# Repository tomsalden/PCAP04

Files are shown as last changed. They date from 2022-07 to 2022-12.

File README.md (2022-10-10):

# ESP32 firmware for the PCAP04

This project has been written as part of a Master's Thesis at the [University of Technology in Delft](https://www.tudelft.nl/). The thesis is based around a Silicon Carbide MEMS pressure sensor. This sensor is a capacitor-based sensor and to read it out, a Capacitor-to-digital converter is necessary. The PCAP04 should work really well due to its high accuracy and resolution. In addition, because it can measure up to 6 capacitances and compare it to one reference capacitance, it is ideal for multiple sensors in the same envionment.
A PlatformIO project has been added to this repository for easy deployment of the code. This contains the latest code written.

# Connecting to the PCAP04

This firmware is written for the ESP32 DevKit-WROOM (available in the Makerspace from the Electrical Engineering Study Association: [Klushok](https://klushok.etv.tudelft.nl/)).

The heart of the firmware uses a library written by Törehan. It has been rewritten to let it make use of I2C in stead of SPI. The reason is that SPI would not work consistenly for my set-up.
The original library can be found on his [GitHub page](https://github.com/torehan/pcap04-arduino).

An example of his integration of the library is visible on his [Metsensor page](https://github.com/torehan/metsensor-pio)

The firmware was first developed for the [PCAP04-EVA-Kit](https://nl.mouser.com/ProductDetail/ScioSense/PCAP04-EVA-KIT?qs=YCa%2FAAYMW01pCMwt%2Fq6O1Q%3D%3D). Later on, the firmware is updated for usage of a custom PCB. In theory, the EVA-Kit should still work with some small modifications. The pinout and further instructions can be found from the section [PCAP04-EVA-board instructions](OldReadme.md). The next sections describe the project using the custom PCB.

# Custom measurement PCB

The PCB has space for three PCAP04 CDC's. Each CDC can read 4 to 5 capacitances and has 1 reference capacitor to make sure the base value is correct.
1 Li-Ion battery will be attached at the back to power the board. Afterwards, the battery is protected and the voltage is boosted to 5V with a HW-775.
As an alternative, one PCAP04 EVA Board can be used instead of one PCAP04 bare chip.

The frontside of the PCB:

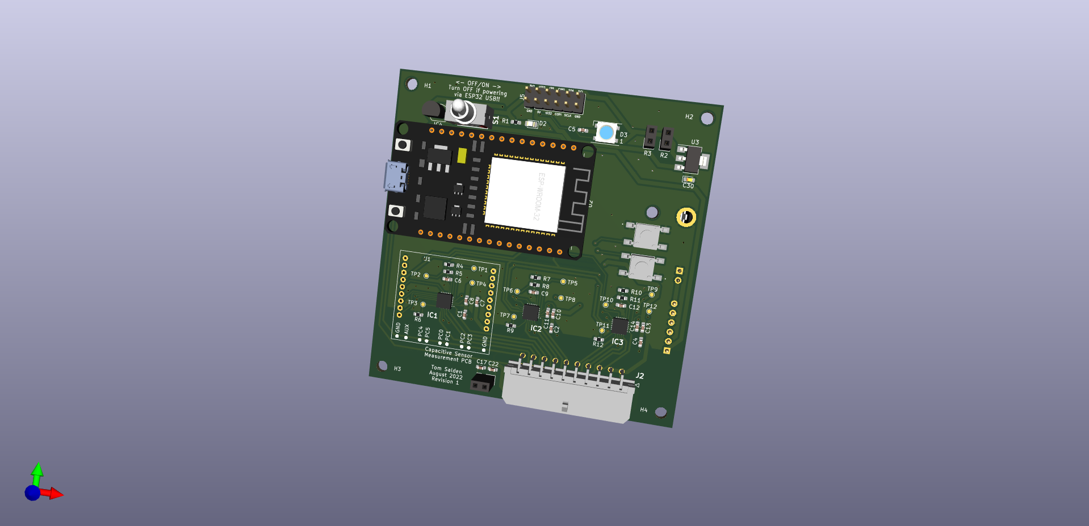
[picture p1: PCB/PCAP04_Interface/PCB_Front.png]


The backside of the PCB:

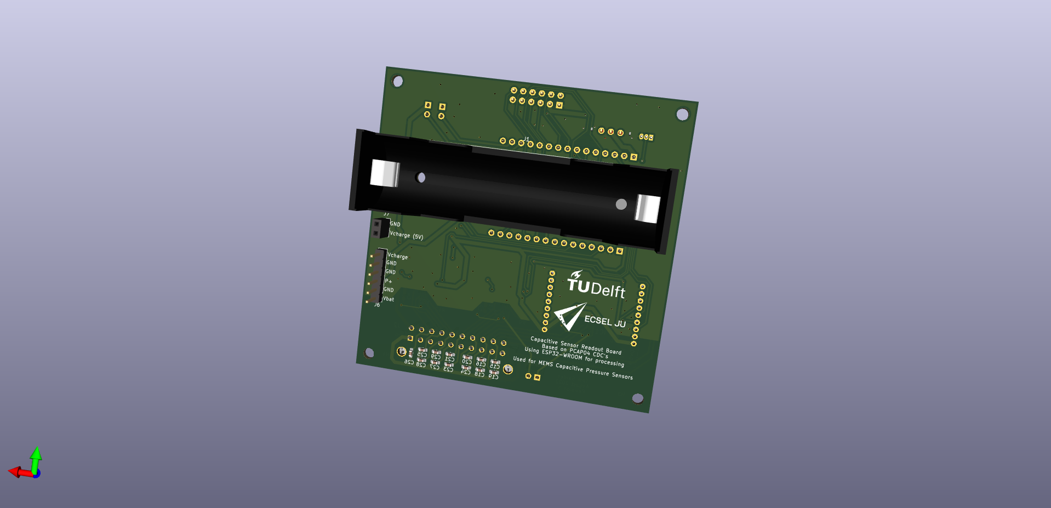
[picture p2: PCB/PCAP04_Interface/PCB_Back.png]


The PCB design includes the following features:

- 3 PCAP04 (or older) measurement chips.
- 1 PCAP04 chip can be replaced with a PCAP04-EVA-BOARD (for testing purposes)
- 3 on-PCB reference capacitors
- 15 (grounded) capacitor measurement possibilities
- Optional offset capacitors can be placed

<!-- -->

- 2 lines for piezoresistive readout are added using voltage dividers
- External resistors can be placed for the voltage division

<!-- -->

- ESP32-Wroom to connect to the PCAP04 chips and process the data
- Micro-SD card holder to save the data
- Power LED directly connected to power line
- RGB Led that is controlled by the ESP32
- 2 multipurpose buttons (start/stop measurements etc.)
- Temperature sensor to keep track of ambient temperature

<!-- -->

- On-off switch breaking the power line
- Can be powered by 2x Li-Ion 18650 batteries (No protection circuitry, use at own risk! Reverse polarity protection is included)
- Cam also be powered by 5V USB line in ESP32-wroom

The Bill of Materials can be found [here]([PCB/PCAP04_Interface/bom/ibom.html](https://tomsalden.github.io/PCAP04/PCB/PCAP04_Interface/bom/ibom.html)) and the order list is placed [here](PCB/PCAP04_Interface/bom/Farnell_Order_List.xlsx).

# Programming instructions
The project has been included in a PlatformIO folder. To setup the workspace, PlatformIO has to be downloaded and this folder has to be imported as a project. This should automatically set the correct libraries and settings. The firmware can be uploaded to an ESP-32 once the project has been imported.

# Program Instructions
Once the firmware has been compiled and uploaded and the PCB has been manufactured, the measurement PCB is ready to start measuring. Place an empty SD card in the SD card slot. Put in a battery in the holder and turn on the switch. The PCB will start its measurements.

## First run
 When the system is turned on, first the program will generate configuration files. Four configuration files in total, one for each PCAP04 chip and one general configuration file.
 
 The general configuration file will define the wifi network the system will try to connect to. The PCAP configuration files define the configuration that can be changed in the webserver.
 
 After this, the system will start with the default settings. It will search for a Wifi Network called "GenericWifi-SSID" with the password "GenericWifi-PWD". If this is not found, then it will create a hotspot.
 Afterwards, the system will apply the default configuration for the PCAP chips and startup a webserver. This can be accessed at the address "192.168.4.1".

 ## Further operation
 Once the system has been stared once, the general configurations file can be edited to let the ESP32 connect to a specified wifi network at startup. If this is not found, the system will create a hotspot.

 Any changes in the webserver settings will immediately be written to the SD card in the corresponding configuration file. This means that at startup, the chips will be loaded with the newest configuration.

 ## Data
 The ESP32 collects the data from all chips. In addition, the system will print a time and a temperature at the time of the measurement. The data file that is generated is a text-based file that can be interpreted as a csv file.

 ### Time
 The measurement of the chips are timed, and the output that will be written will correspond to the time they are taken.
 Because the system does not have a Real Time Clock (RTC), the ESP32 does not know the time at startup. Therefore, the default time is set at October 18 2022 at 0:00. To set the time and date to the correct moment, connect to the webserver and press the "Set Current Time" button. From that moment on, the time will be synchronised with the device that pressed on that button until the ESP32 is restarted.

 ### Temperature
 The temperature on the PCB is measured using a MCP-9701. The voltage reading is converted to a temperature and saved in the data files.

 ### Capacitance data
 The capacitance of each pin of every PCAP chip is read out as fast as possible. When this is done, the data is collected and written to the data file.

## Indication LED
The PCB features an indication LED. This LED shows the status of the program.
After startup and configuration, the measurement starts and the LED will blink blue-green.

# Features and Future improvements

✅Ability to connect to and read data from PCAP04

✅Ability to change I2C address on demand

✅Read data synchronously with PCAP04, as recommended in the datasheet

✅Add SD-card to the system to log data

✅Place PCAP04 settings file on SD card

✅Create a PCB for this system

✅Edit PCAP04 settings without reflashing ESP32

✅Create webserver-based interface for ESP32 (for config changes)

✅Allow for three PCAP04 devices at the same time

✅Clean up code for deployment

⬜️~~Automatically change output format depending on mode selection~~

⬜️~~Make a csv file automatically from the output~~

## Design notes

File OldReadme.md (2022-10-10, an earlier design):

# PCAP04-EVA-board instructions

## Interconnections PCAP04-Dev-Kit and ESP32 DevKit-WROOM

The interconnects used for the current firmware. The following images show the pinout of the [ESP32 board](https://raw.githubusercontent.com/AchimPieters/esp32-homekit-camera/master/Images/ESP32-30PIN-DEVBOARD.png) and the PCAP04.

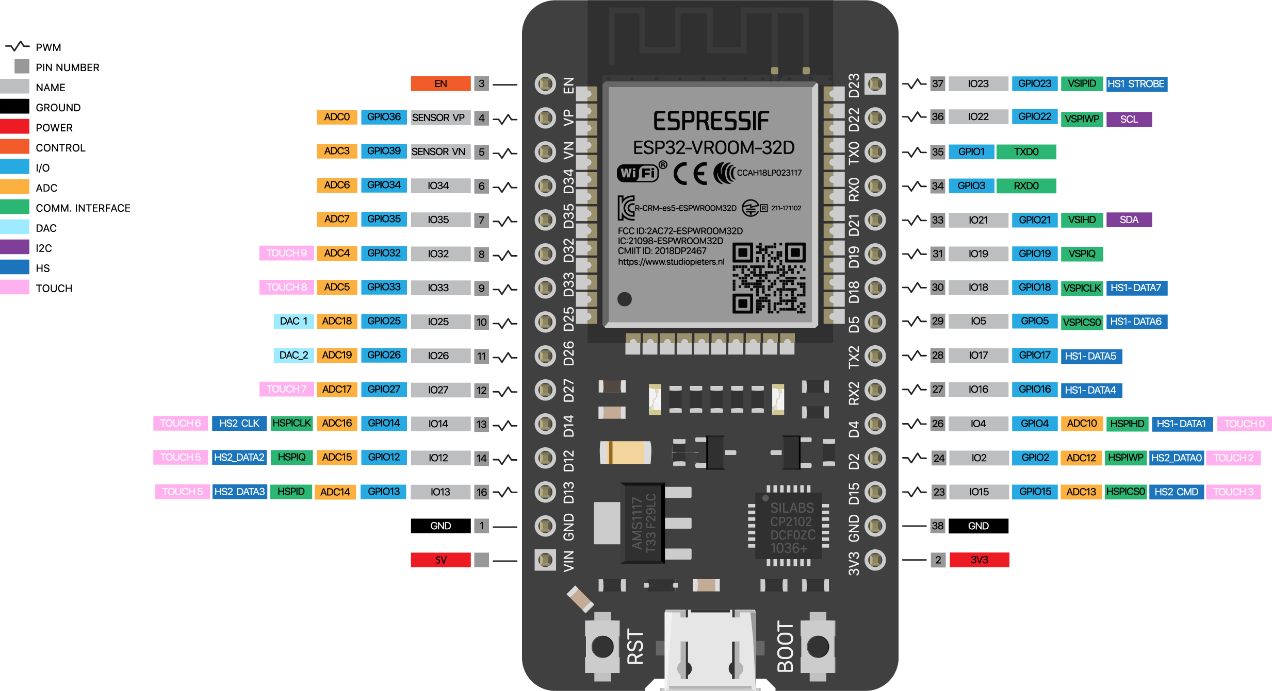
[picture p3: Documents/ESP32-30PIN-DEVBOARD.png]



### Power

| ESP32 | PCAP04                               |
| ----- | ------------------------------------ |
| 3V3   | VDD (J1.1 or J2.1)                   |
| GND   | GND (J1.2, J1.9, J2.2, J2.7 or J2.9) |

### Communication

| ESP32          | PCAP04          |
| -------------- | --------------- |
| 3V3            | IIC_EN (J2.3)   |
| GPIO21-I2C SDA | MOSI_SDA (J2.4) |
| GPIO22-I2C SCL | SCK_SCL (J2.6)  |

| ESP32            | SD-Card Reader |
| ---------------- | -------------- |
| 3V3              | +3.3           |
| GND              | GND            |
| GPIO5-VSPI CS0   | CS             |
| GPIO18-VSPI CLK  | SCK            |
| GPIO19-VSPI MISO | MISO           |
| GPIO23-VSPI MOSI | MOSI           |

### GPIO connections

| ESP32  | PCAP04     |
| ------ | ---------- |
| GPIO2  | PG5 (J1.8) |
| GPIO4  | PG4 (J1.7) |
| GPIO16 | PG3 (J1.6) |
| GPIO17 | PG2 (J1.5) |

### Other connections

| ESP32  | Interface |
| ------ | --------- |
| GPIO32 | Led Blue  |
| GPIO33 | Led Green |
| GPIO26 | Led Red   |
| GPIO27 | Power Led |

## Flashing the firmware

For flashing the firmware, the basic Arduino IDE can be used. The board settings used are:

- Board:            Node32s
- Upload Speed:     921600
- Flash Frequency   80MHz
- Partition Scheme  Default
- Core Debug Level  None

## Using the Set-up

At this point in time, the set-up works via the serial monitor and a limited web-interface. The following will happen at startup:

1. The ESP32 will startup, displayed with the Power Led. Either it will connect to a known network or start its own network.
2. The ESP32 will test if an SD card is available. It will create a new file for data storage. If the SD-card is not available, the indicator light will flash red three times.
3. The ESP32 will check if a config file is present on the SD. If so, the config will be loaded. Otherwise, a new file will be created with the standard configuration.
4. The ESP will test the I2C connection to the PCAP04. If there is a problem, a red light will appear. Otherwise the light turns blue
5. The ESP will initialise the PCAP04 and write the correct configuration to the chip. Once done, the Led turns green
6. After initialisation, the PCAP04 will start its measurements. The ESP32 will retreive a new measurement every second, indicated by a flashing red-green light.
7. If an SD-card is available, the ESP32 will save the data as in a .csv format on the card. In addition, the ESP32 will display the current measurement values in the serial port. (If a more complete output is necessary, uncomment line 204 in the [PCAP04.ino](https://github.com/tomsalden/PCAP04/blob/main/PCAP04.ino#L192) file and comment the Print for Excel lines.)

Now, the Serial Port of the Arduino IDE can be used to readout the values.
In addition, the [Data Streamer](https://support.microsoft.com/nl-nl/office/wat-is-data-streamer-1d52ffce-261c-4d7b-8017-89e8ee2b806f) in Excel can record, process and save live data.

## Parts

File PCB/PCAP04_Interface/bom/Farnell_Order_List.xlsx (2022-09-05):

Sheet: Sheet1
Part Number | Quantity | Description | Price/piece | Price total | Other websites | Part name | Quantity | website | Price/piece | Piece total
2896375 | 30 | SMD Multilayer Ceramic Capacitor, 1 pF | €0.1080 | €3.2400 |  | WS2812B (https://www.vanallesenmeer.nl/WS2812B-5050-RGB-LED-with-Integrated-Driver-Chip-10-Pack-Adafruit-1655) | 1 | vanallesenmeer | €8.35 | €8.35 | Total
2134025 | 6 | SMD Multilayer Ceramic Capacitor, 2 pF | €0.3230 | €1.9380 |  | Verzendkosten | 1 | vanallesenmeer | €2.00 | €2.00 | €145.49
2672793 | 6 | SMD Multilayer Ceramic Capacitor, IR Reflow, 10000 | €0.1180 | €0.7080 |  | AMS1117 3V3 (https://www.tinytronics.nl/shop/en/components/voltage-regulators/ams1117-3.3v-voltage-regulator-sot-223) | 2 | tinytronics | €0.50 | €1.00
2494230 | 10 | SMD Multilayer Ceramic Capacitor, 10 µF | €0.0589 | €0.5890 |  | Li-Ion Charging circuit (https://www.tinytronics.nl/shop/en/power/bms-and-chargers/li-ion-and-li-po/with-protection-circuit/li-ion-charge-and-protection-circuit-2100ma-with-dc-dc-conv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) | 2 | tinytronics | €4.00 | €8.00
3416132 | 10 | SMD Multilayer Ceramic Capacitor, 4.7 µF | €0.1130 | €1.1300 |  | 18650 battery holder (https://www.tinytronics.nl/shop/en/power/battery-holders-and-clips/18650/1x-18650-battery-holder-for-pcb) | 2 | tinytronics | €1.50 | €3.00
2672791 | 2 | SMD Multilayer Ceramic Capacitor, IR Reflow, 0.1 µF | €0.2360 | €0.4720 |  | Verzendkosten | 1 | tinytronics | €2.50 | €2.50
197427 | 5 | Surface Mount Tantalum Capacitor, 10 µF | €0.3000 | €1.5000
2331324 | 2 | SMD Chip Resistor, 64.9 ohm | €0.3990 | €0.7980
3796325 | 5 | LED, Red, SMD | €0.1210 | €0.6050
1466783 | 8 | Standoff, Zinc Plated | €0.4610 | €3.6880
3397776 | 10 | Tactile Switch, FSMJSM | €0.2850 | €2.8500
1439483 | 2 | Temperature Sensor IC, Voltage, ± 2°C, 0 °C, 70 °C, TO-92, 3 Pins | €0.4800 | €0.9600
 |  |  |  | €0.0000
 |  |  |  | €0.0000
Mouser
Part Number | Quantity | Description | Price/piece | Price total
985-PCAP04-AQFM-24 | 10 | PCAP04 | €6.8600 | €68.6000
118-2MS1T2B3M2QES | 2 | Toggle Switch | €3.1700 | €6.3400
538-43045-2022 | 2 | Headers & Wire Housings Microfit 3.0 | €8.2100 | €16.4200
640-MEM20670218000A | 2 | Micro SDCard Holder | €1.1400 | €2.2800
DigiKey
Part Number | Quantity | Description | Price/piece | Price total
BH-18650-PC-ND | 2 | 18650 Battery holder | €4.2600 | €8.5200

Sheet: EverythingMouser
Mouser number | Manufactuer number | Quantity | Description | Price/piece | Price total
77-VJ0603A1R0BXACBC | VJ0603A1R0BXACW1BC | 30 | SMD Multilayer Ceramic Capacitor, 1 pF | €0.114 | €3.42
77-VJ0603D2R0BXPAJ | VJ0603D2R0BXPAJ | 6 | SMD Multilayer Ceramic Capacitor, 2 pF | €0.470 | €2.82
791-0603B103K101CT | 0603B103K101CT | 10 | SMD Multilayer Ceramic Capacitor, IR Reflow, 10000 | €0.029 | €0.29
81-R188R60J106KE7D | GRM188R60J106KE47D | 10 | SMD Multilayer Ceramic Capacitor, 10 µF | €0.059 | €0.59
810-C1608X7S1A475MAC | C1608X7S1A475M080AC | 10 | SMD Multilayer Ceramic Capacitor, 4.7 µF | €0.119 | €1.19
80-C0603C104J4R | C0603C104J4RACTU | 2 | SMD Multilayer Ceramic Capacitor, IR Reflow, 0.1 µF | €0.100 | €0.20
581-F981A226MMALZT | F981A226MMALZT | 2 | Surface mount talantum Cap 22uF | €0.700 | €1.40
667-ERA-3AEB64R9V | ERA-3AEB64R9V | 2 | SMD Chip Resistor, 64.9 ohm | €0.350 | €0.70
710-150080RS75000 | 150080RS75000 | 5 | LED, Red, SMD | €0.190 | €0.95
710-970250321 | 970250321 | 8 | Standoff, Zinc Plated | €0.580 | €4.64
506-FSM2JSMAATR | FSM2JSMAATR | 4 | Tactile Switch, FSMJSM | €0.320 | €1.28
579-MCP9701-E/TO | MCP9701-E/TO | 2 | Temperature Sensor IC, Voltage, ± 2°C, 0 °C, 70 °C, TO-92, 3 Pins | €0.570 | €1.14
48SM003 | 48SM003 | 8 | M3 screw | €0.194 | €1.55
985-PCAP04-AQFM-24 | PCAP04-AQFM-24 | 10 | PCAP04 | €6.16 | €61.60
118-2MS1T2B3M2QES | 2MS1T2B3M2QES | 2 | Toggle Switch | €3.17 | €6.34
538-43045-2022 | 43045-2022 | 2 | Headers & Wire Housings Microfit 3.0 | €8.21 | €16.42
640-MEM20670218000A | MEM2067-02-180-00-A | 2 | Micro SDCard Holder | €1.14 | €2.28
485-4684 | 4684 | 1 | 2020 RGB LEDs - 10-pack - WS2812B | €3.95 | €3.95
637-LDI1117-3.3H | LDI1117-3.3H | 2 | 3.3 LDO | €1.960 | €3.92
538-43025-2000 | 43025-2000 | 5 | Mouser recepticle | €1.330 | €6.65
538-43030-0004-CT | 43030-0004 (Cut Strip) | 100 | Mouser contacts | €0.082 | €8.20
Shopping cart link | https://nl.mouser.com/ProjectManager/ProjectDetail.aspx?AccessID=6550a5fe31 |  |  |  | €129.53

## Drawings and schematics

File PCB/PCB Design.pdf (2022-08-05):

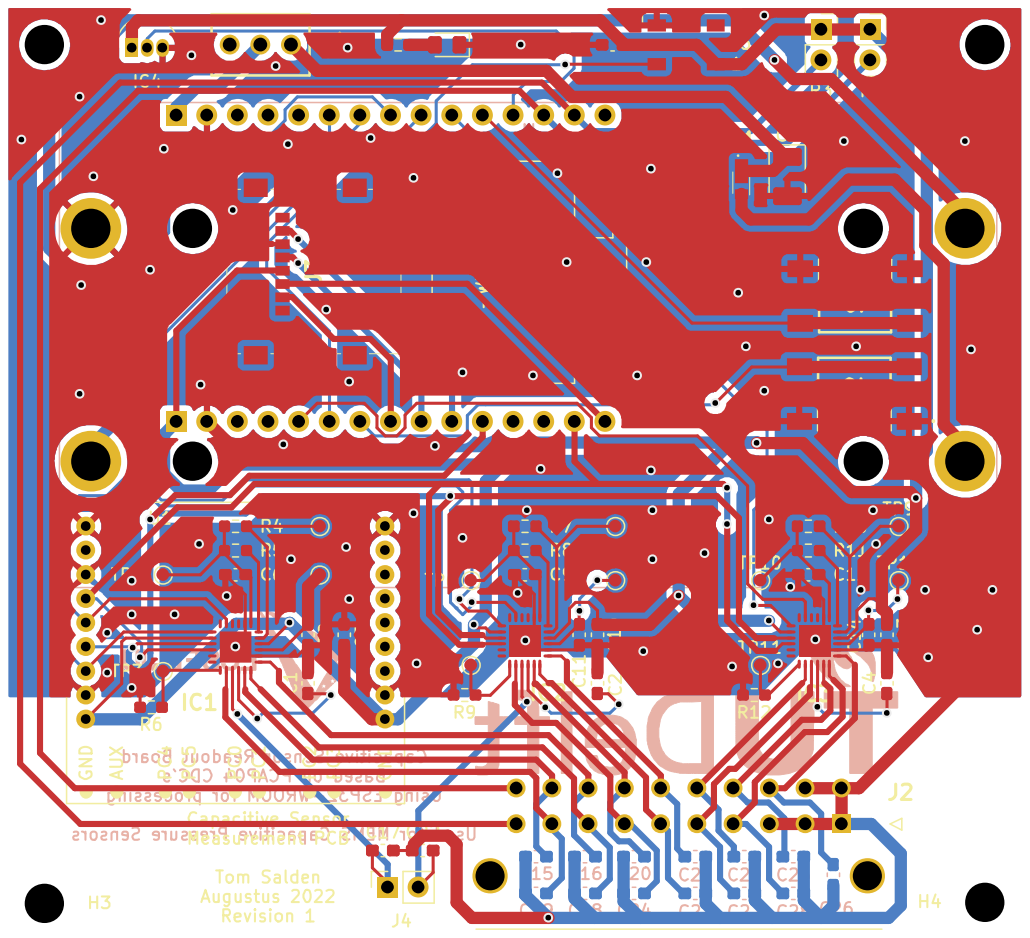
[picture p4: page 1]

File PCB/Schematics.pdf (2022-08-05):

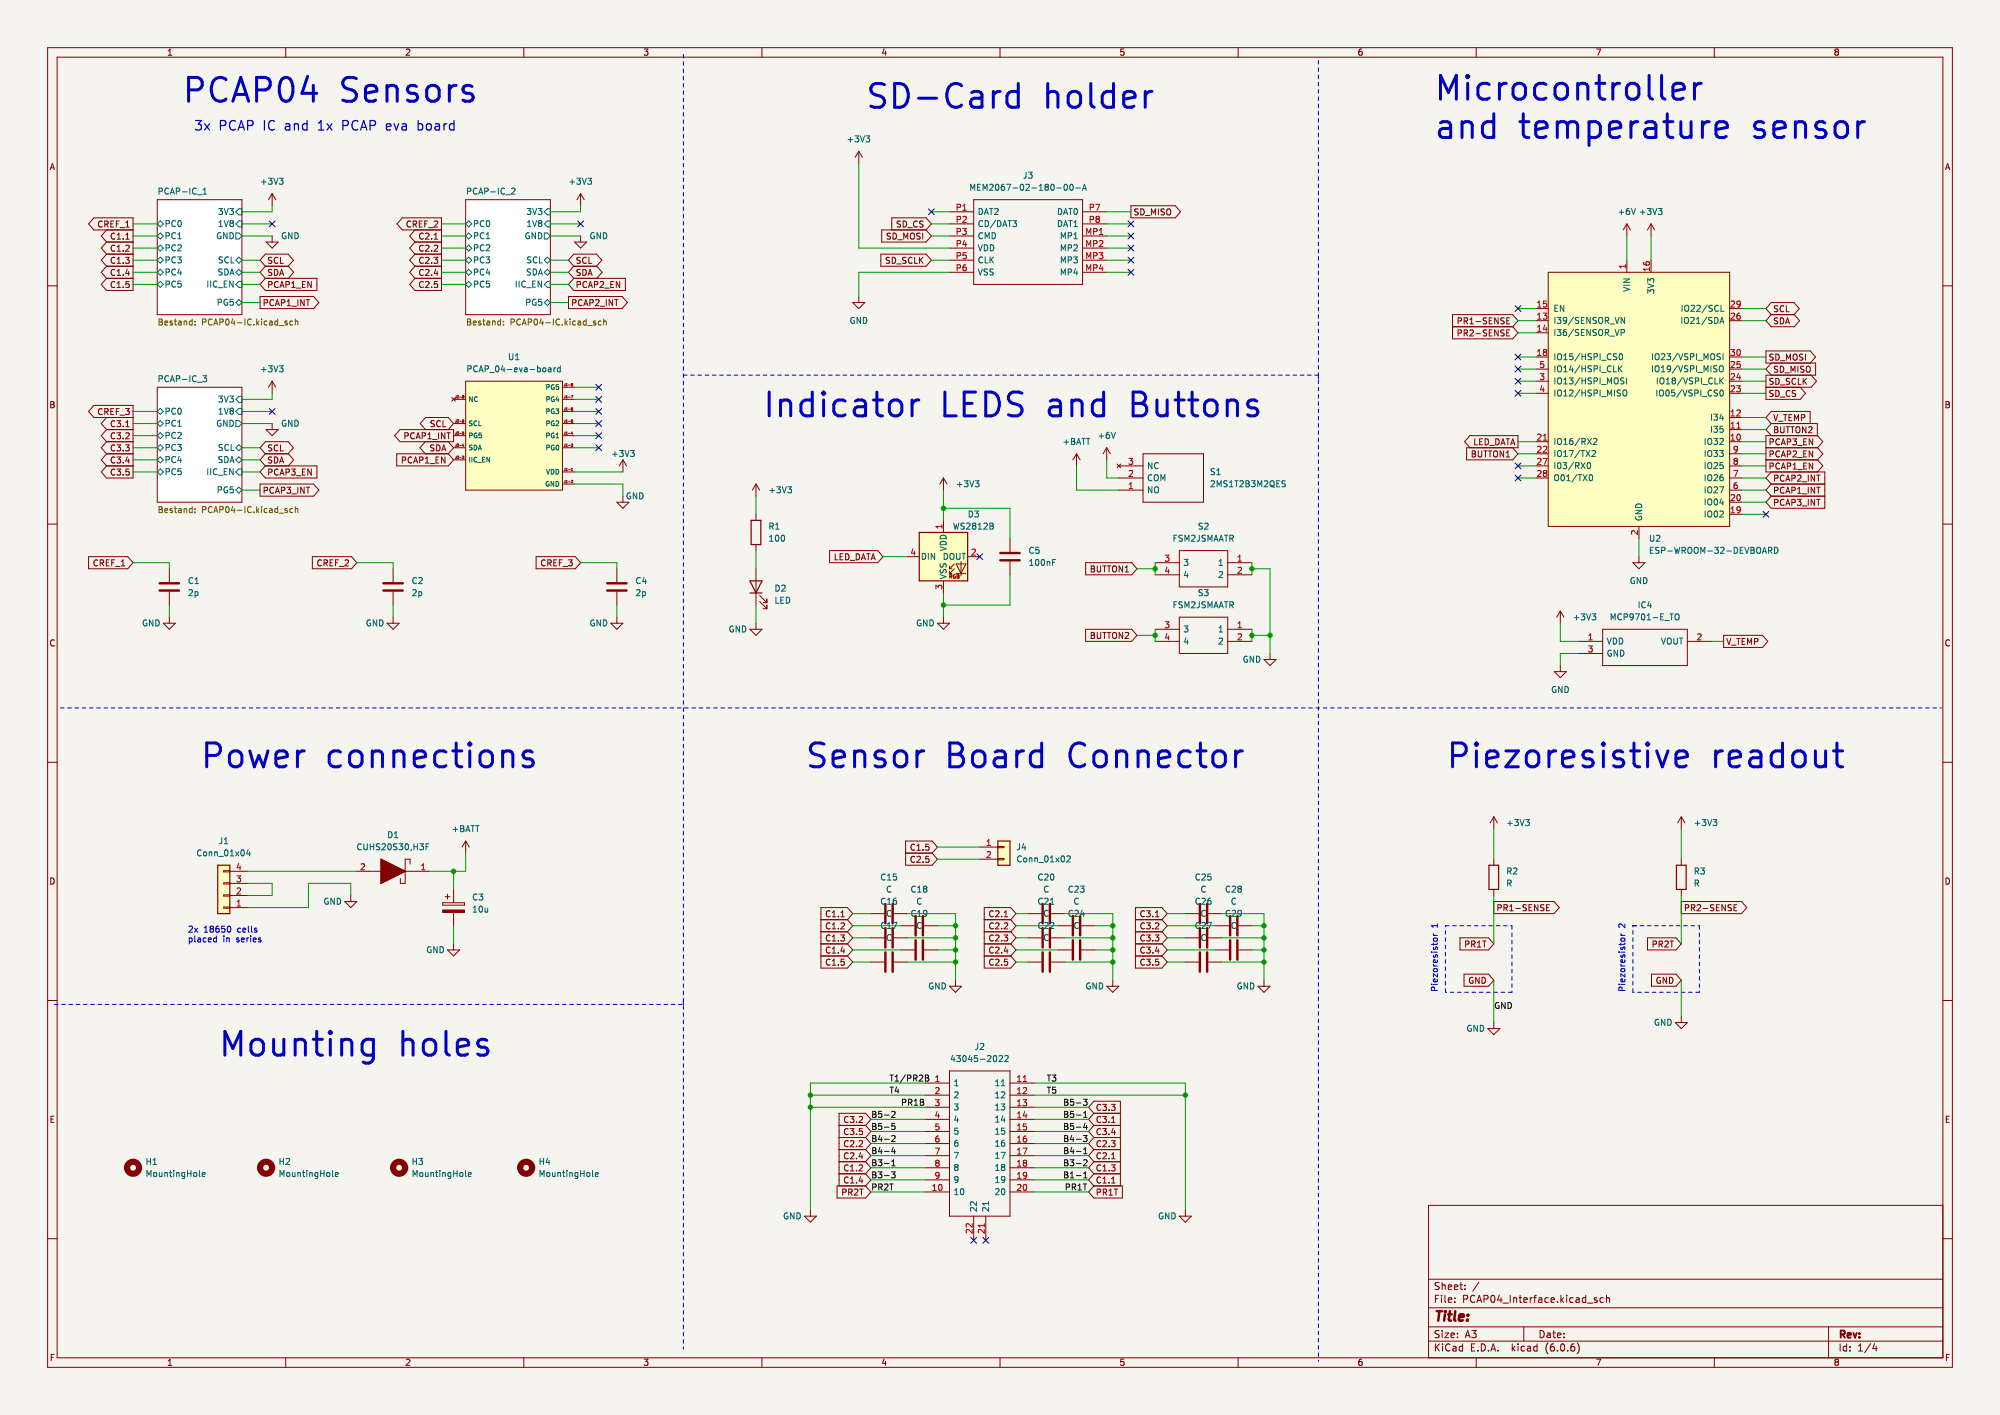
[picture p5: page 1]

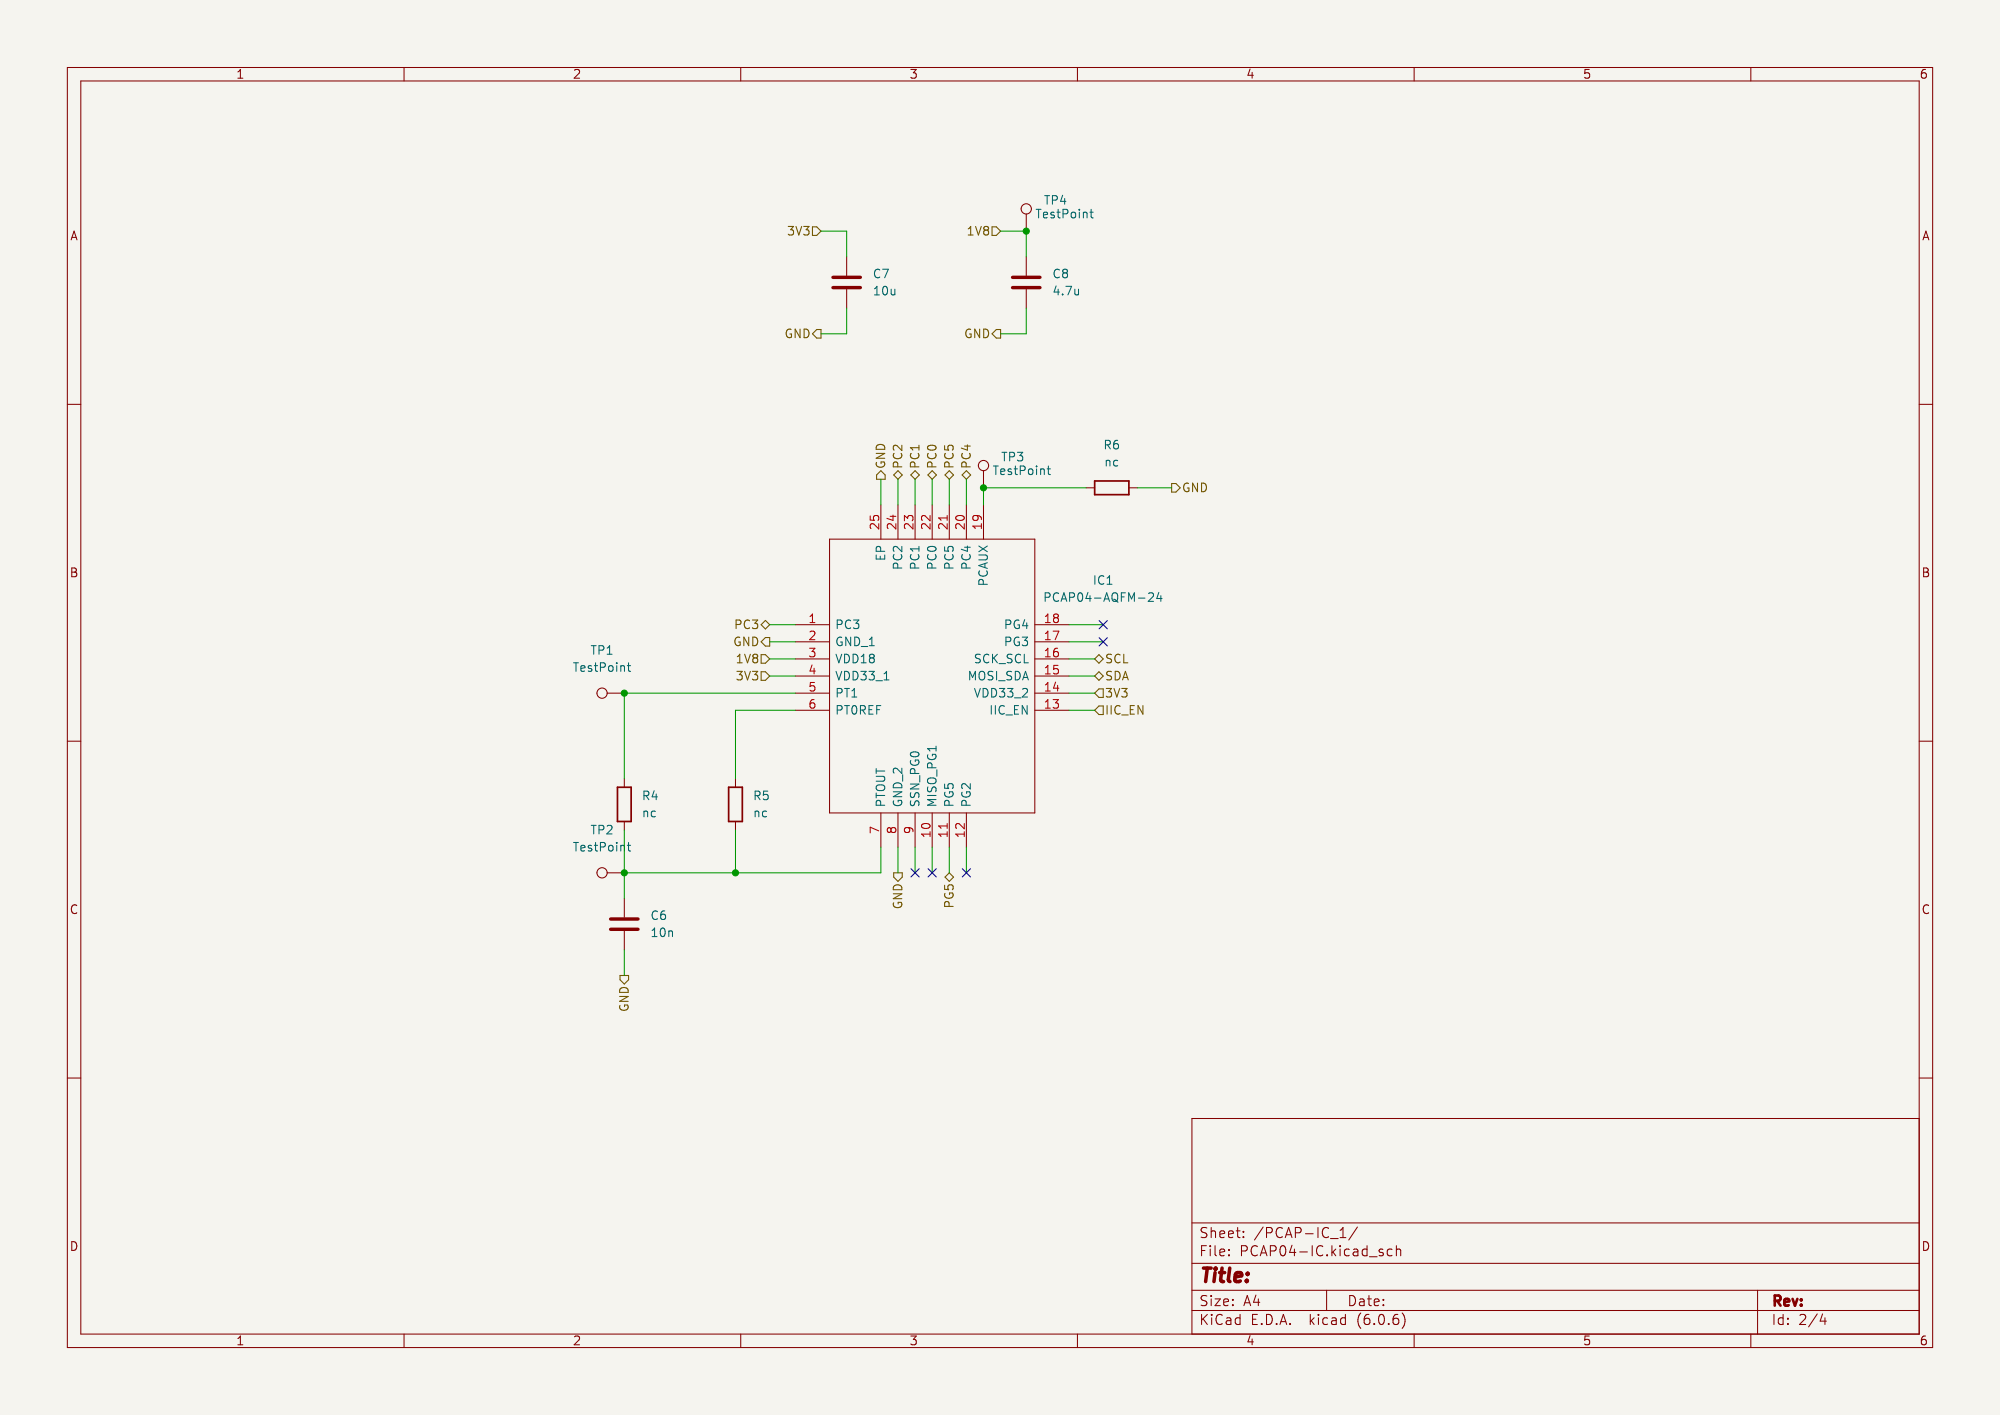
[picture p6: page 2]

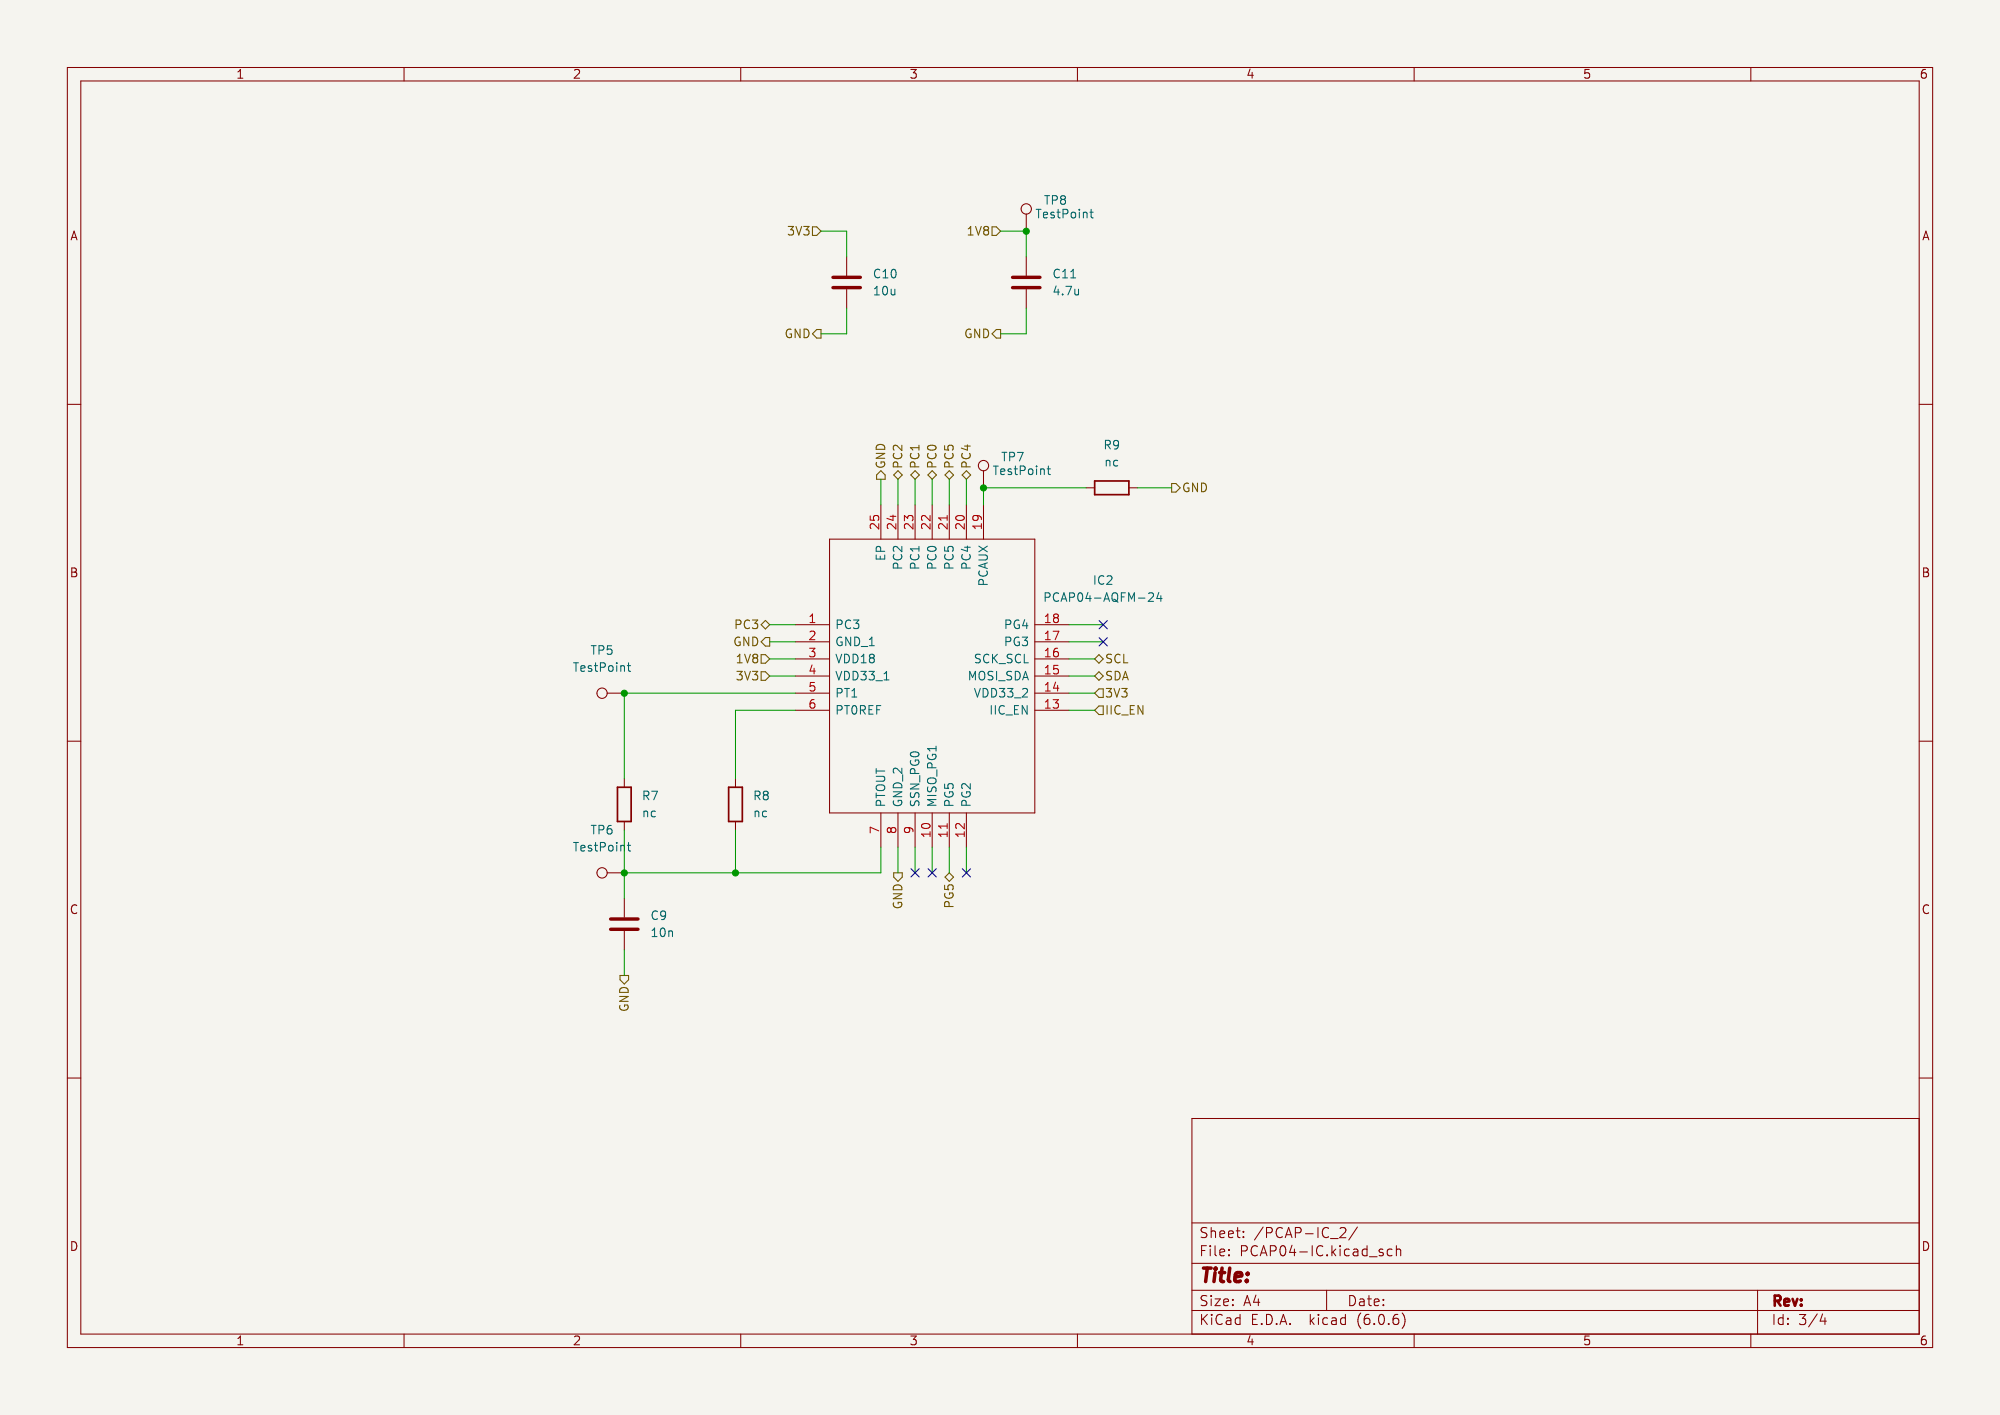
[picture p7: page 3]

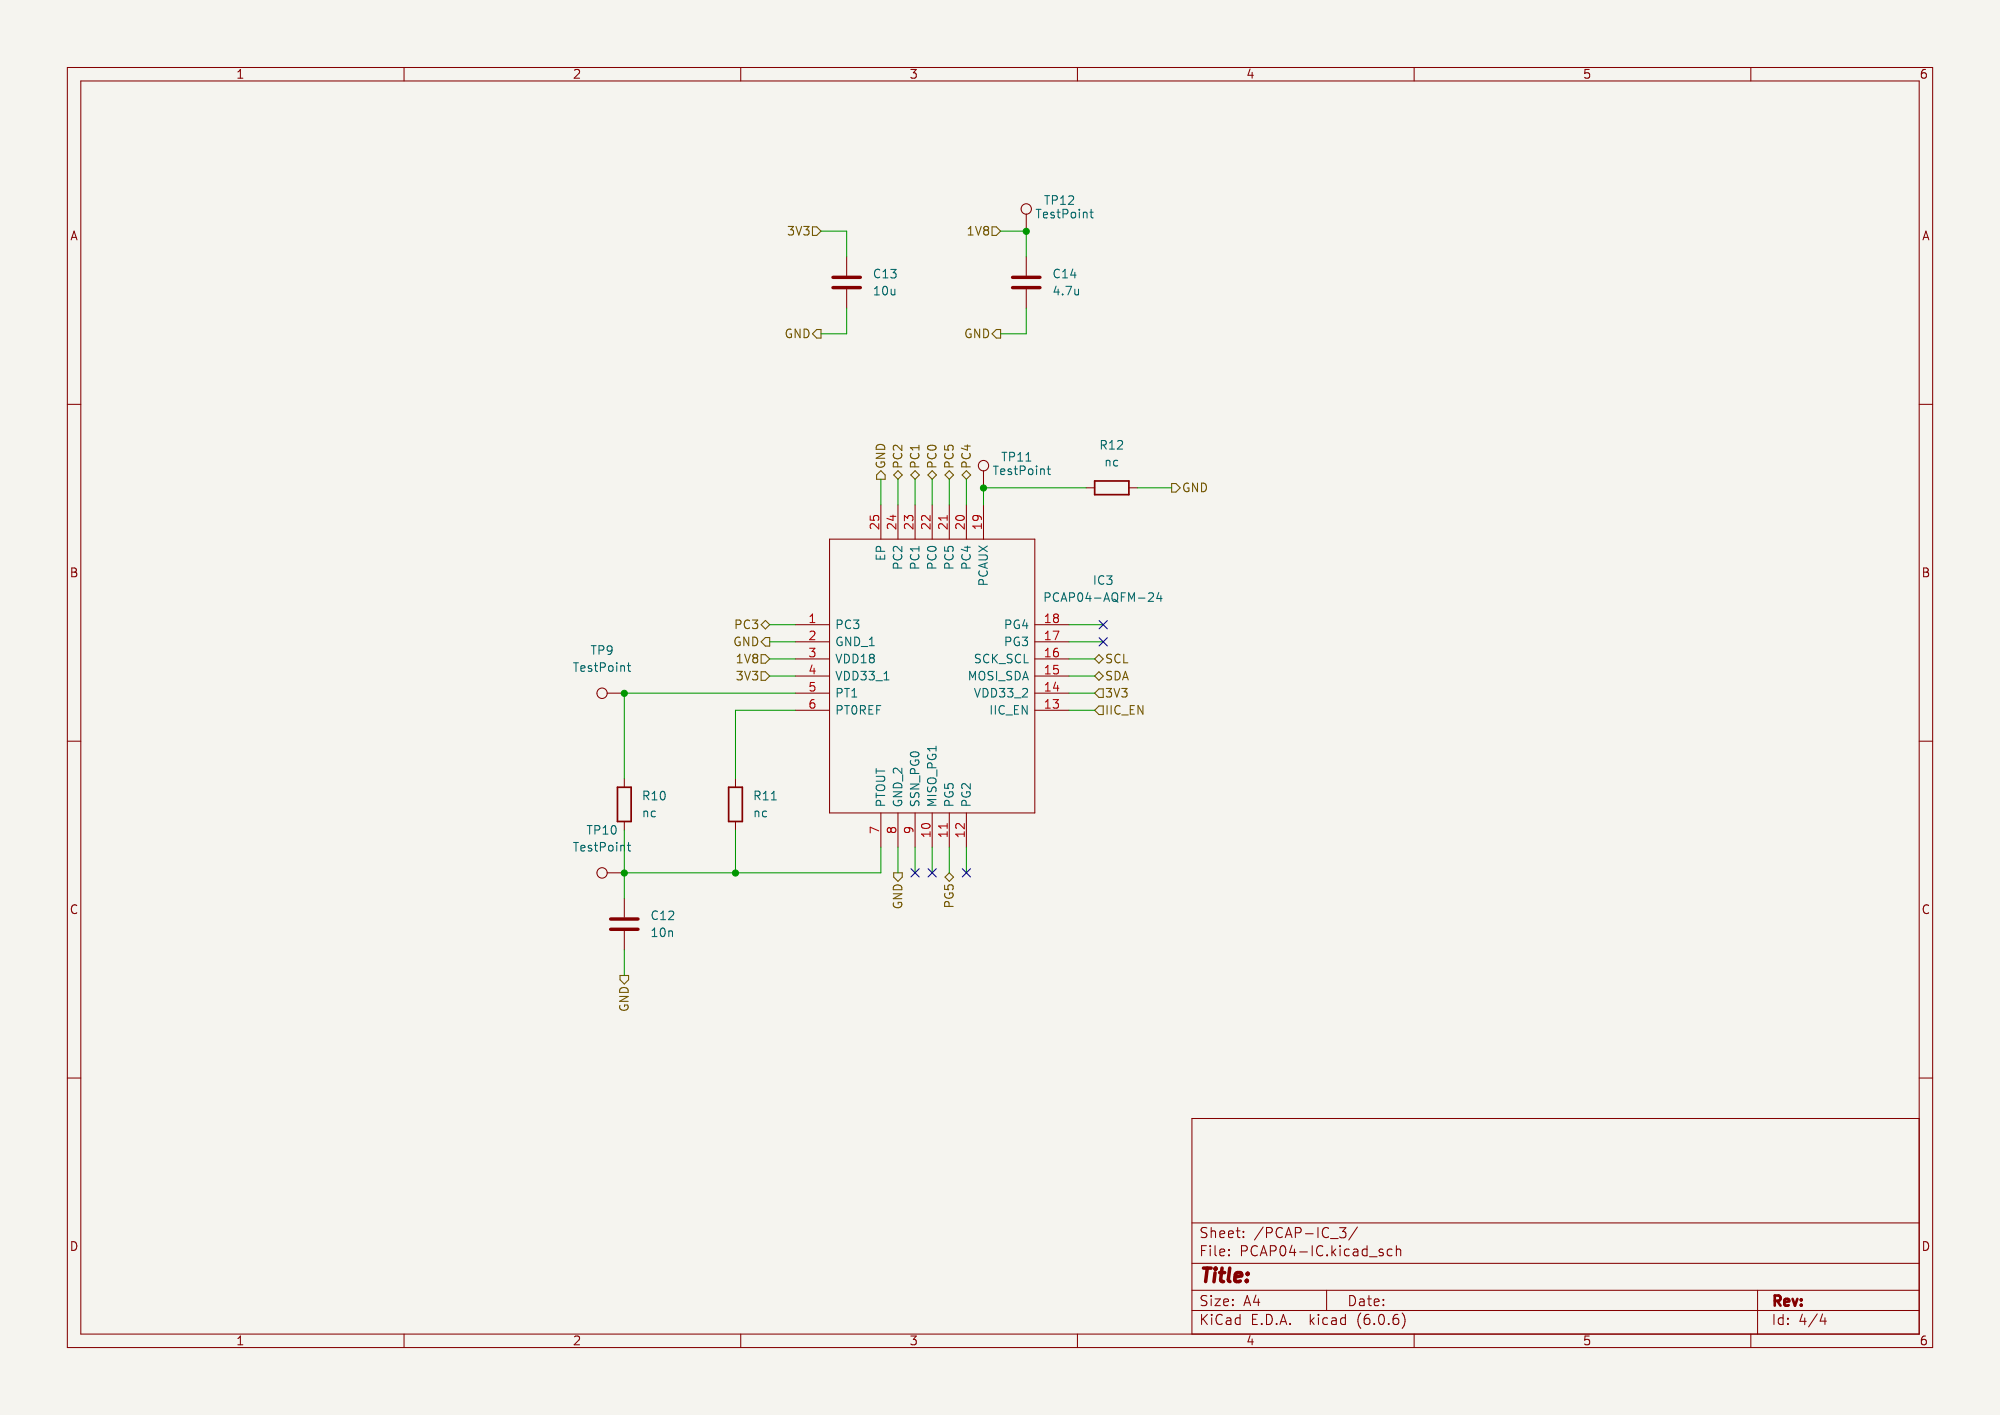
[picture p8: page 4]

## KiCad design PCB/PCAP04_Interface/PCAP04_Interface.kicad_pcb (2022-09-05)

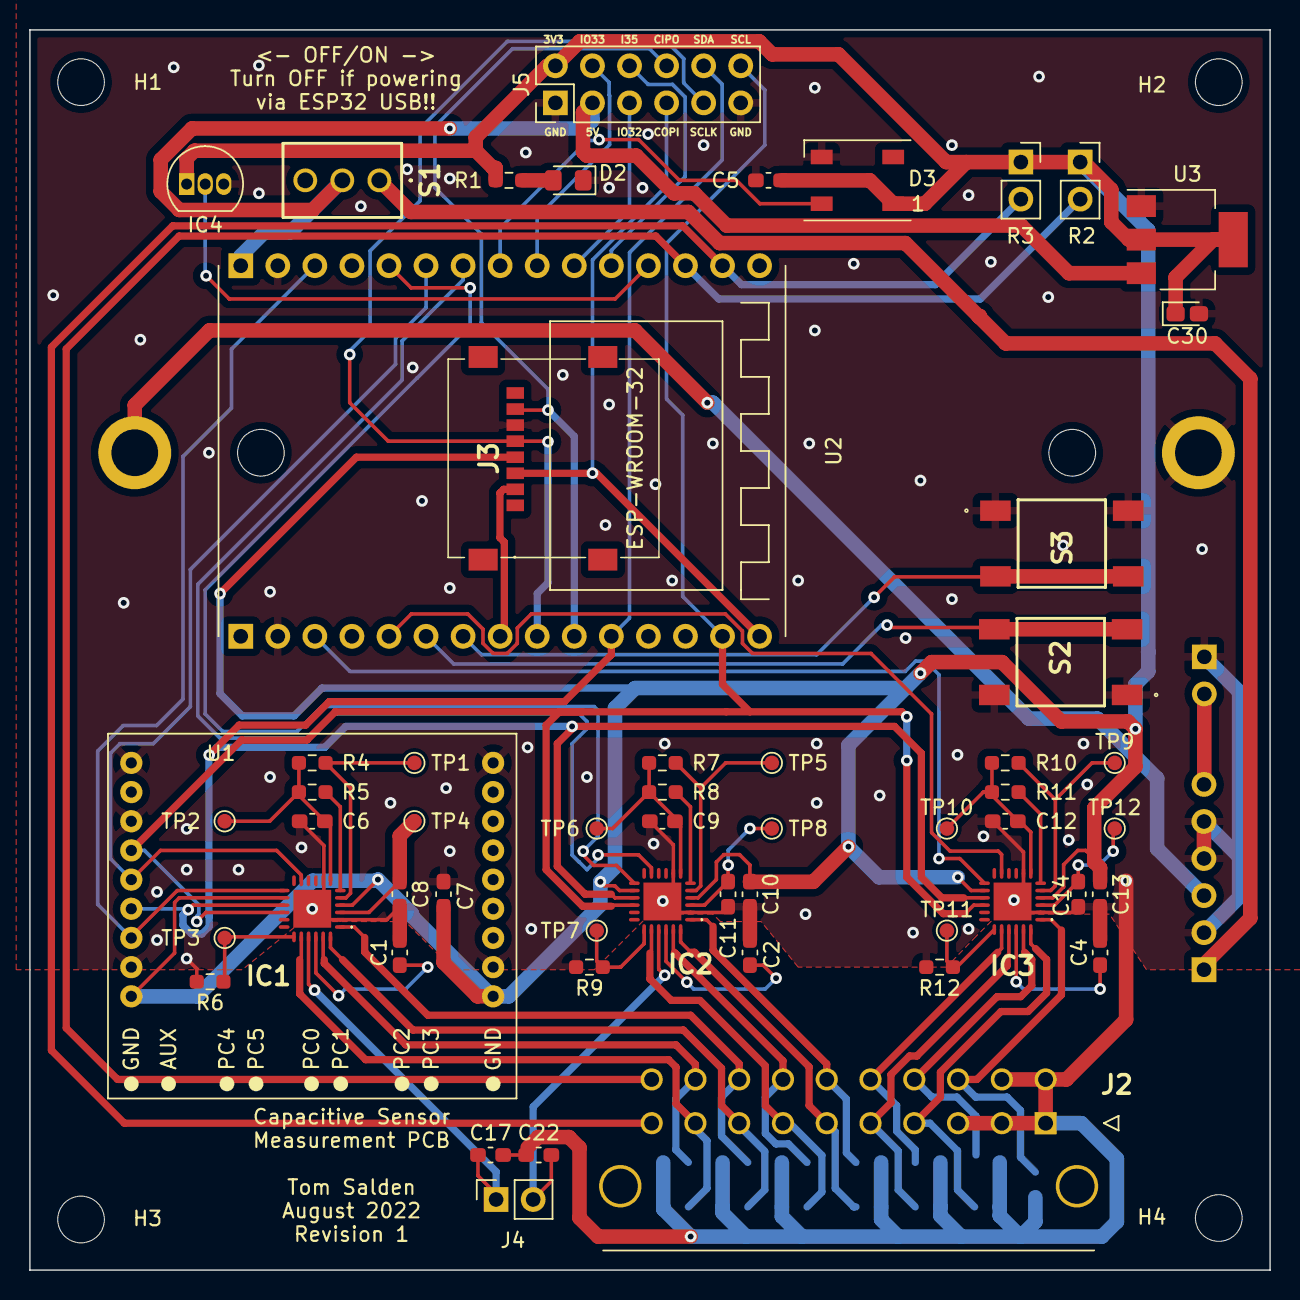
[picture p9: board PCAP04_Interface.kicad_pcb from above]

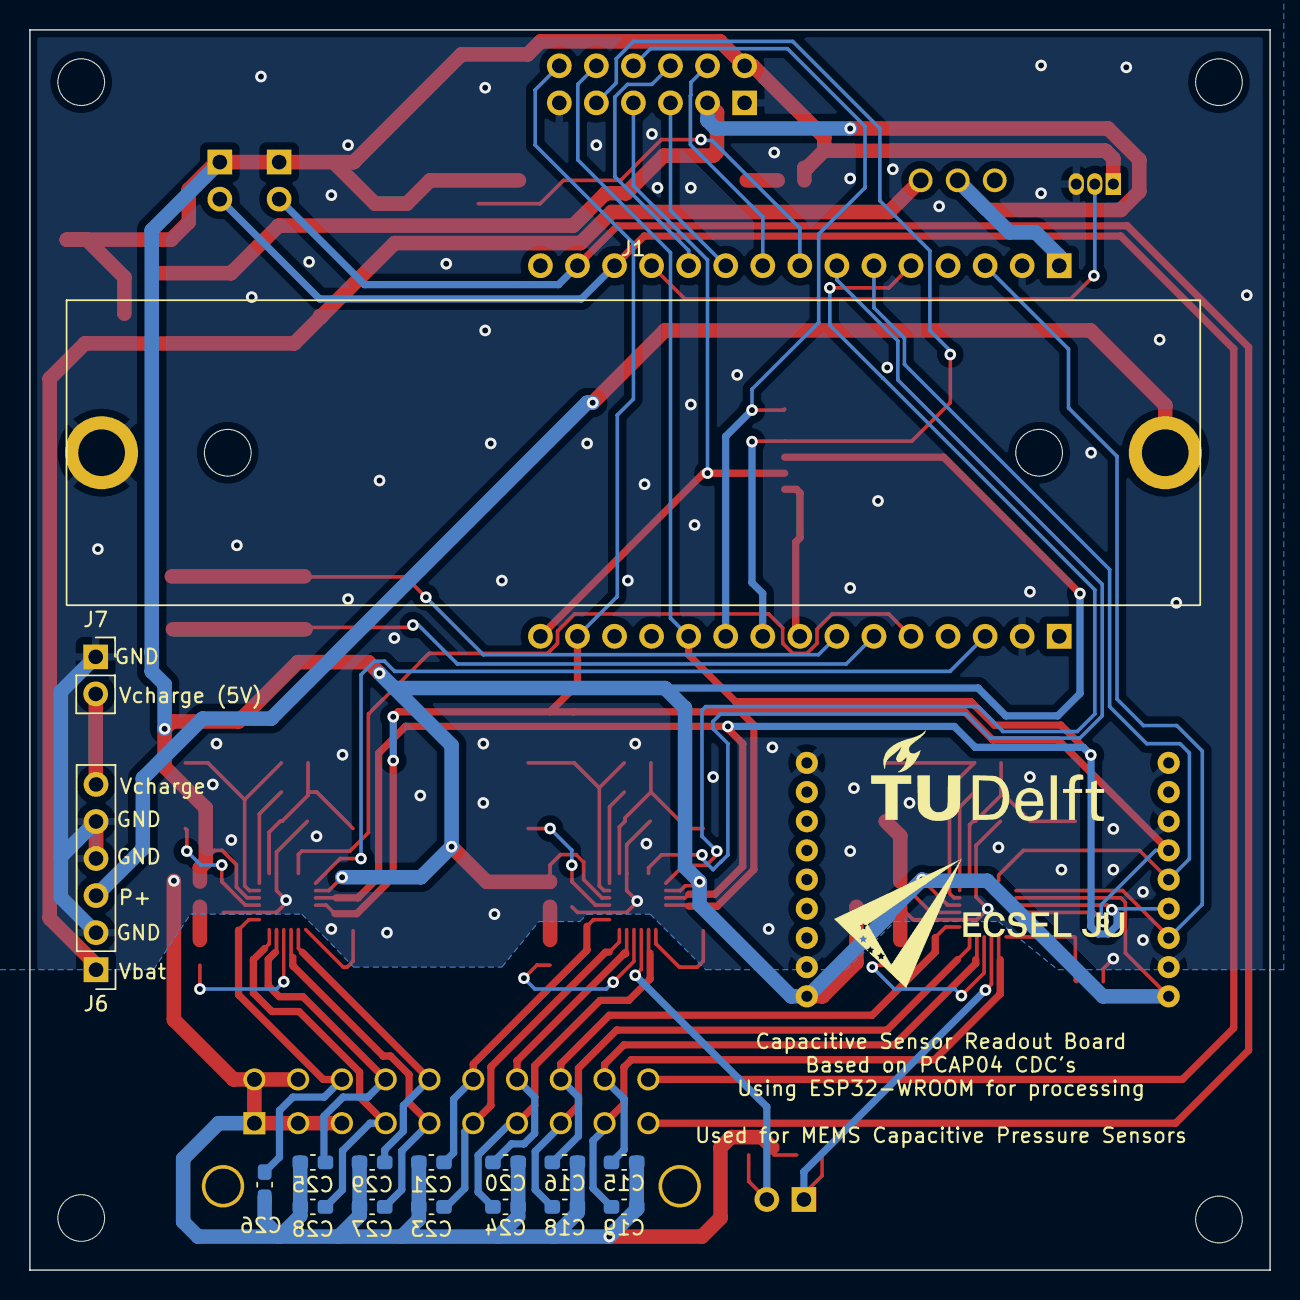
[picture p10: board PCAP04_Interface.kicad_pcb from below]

Board: 2 copper layers, 85.0 x 85.0 mm, 76 parts (16 on the bottom side), 61 nets.

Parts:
C1, C2, C4: 2p; C_0603_1608Metric_Pad1.08x0.95mm_HandSolder
C5: 100nF; C_0603_1608Metric_Pad1.08x0.95mm_HandSolder
C6, C9, C12: 10n; C_0603_1608Metric_Pad1.08x0.95mm_HandSolder
C7, C10, C13: 10u; C_0603_1608Metric_Pad1.08x0.95mm_HandSolder
C8, C11, C14: 4.7u; C_0603_1608Metric_Pad1.08x0.95mm_HandSolder
C15, C16, C17, C18, C19, C20, C21, C22, C23, C24, C25, C26, C27, C28, C29: C; C_0603_1608Metric_Pad1.08x0.95mm_HandSolder
C30: 22u; CP_EIA-1608-10_AVX-L_Pad1.25x1.05mm_HandSolder
D2: LED; LED_0805_2012Metric_Pad1.15x1.40mm_HandSolder
D3: WS2812B; LED_WS2812B_PLCC4_5.0x5.0mm_P3.2mm
H1, H2, H3, H4: MountingHole; MountingHole_3.2mm_M3
IC1, IC2, IC3: PCAP04-AQFM-24; PCAP04AQFM24
IC4: MCP9701-E_TO; TO-92_Inline
J1: Conn_01x02; BH-18650-PC
J2: 43045-2022; 43045-20_21,22,23_
J3: MEM2067-02-180-00-A; MEM20670218000A
J4, J7: Conn_01x02; PinSocket_1x02_P2.54mm_Vertical
J5: Conn_02x06_Odd_Even; PinHeader_2x06_P2.54mm_Vertical
J6: Li-ion Charge and Protection circuit; PinHeader_1x06_P2.54mm_Vertical
R1: 100; R_0603_1608Metric_Pad0.98x0.95mm_HandSolder
R2, R3: R; PinSocket_1x02_P2.54mm_Vertical
R4, R5, R6, R7, R8, R9, R10, R11, R12: nc; R_0603_1608Metric_Pad0.98x0.95mm_HandSolder
S1: 2MS1T2B3M2QES
S2, S3: FSM2JSMAATR; FSM2J_1
TP1, TP2, TP3, TP4, TP5, TP6, TP7, TP8, TP9, TP10, TP11, TP12: TestPoint; TestPoint_Pad_D1.0mm
U1: PCAP_04-eva-board
U2: ESP-WROOM-32-DEVBOARD
U3: AMS1117-3.3; SOT-223-3_TabPin2

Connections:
+3V3: C5.1, C7.1, C10.1, C13.1, C30.1, D3.1 (VDD), IC1.4 (VDD33_1), IC1.14 (VDD33_2), IC2.4 (VDD33_1), IC2.14 (VDD33_2), IC3.4 (VDD33_1), IC3.14 (VDD33_2), IC4.1 (VDD), J3.P4 (VDD), J5.2, R1.1, R2.1, R3.1, U1.J1-1 (VDD), U1.J2-1 (VDD), U3.2 (VO)
+6V: J5.3, S1.2 (COM), U2.1 (VIN), U3.3 (VI)
+BATT: J6.1, S1.1 (NO)
/PCAP-IC_1/1V8: C8.1, IC1.3 (VDD18), TP4.1
/PCAP-IC_2/1V8: C11.1, IC2.3 (VDD18), TP8.1
/PCAP-IC_3/1V8: C14.1, IC3.3 (VDD18), TP12.1
B+: J1.2, J6.3
BUTTON1: S2.3, S2.4, U2.21 (IO16/RX2)
BUTTON2: S3.3, S3.4, U2.22 (IO17/TX2)
C1.1: C15.2, IC1.23 (PC1), J2.19
C1.2: C18.2, IC1.24 (PC2), J2.8
C1.3: C16.2, IC1.1 (PC3), J2.18
C1.4: C19.2, IC1.20 (PC4), J2.9
C1.5: C17.2, IC1.21 (PC5), J4.1
C2.1: C20.2, IC2.23 (PC1), J2.17
C2.2: C23.2, IC2.24 (PC2), J2.6
C2.3: C21.2, IC2.1 (PC3), J2.16
C2.4: C24.2, IC2.20 (PC4), J2.7
C2.5: C22.2, IC2.21 (PC5), J4.2
C3.1: C25.2, IC3.23 (PC1), J2.14
C3.2: C28.2, IC3.24 (PC2), J2.4
C3.3: C26.2, IC3.1 (PC3), J2.13
C3.4: C29.2, IC3.20 (PC4), J2.15
C3.5: C27.2, IC3.21 (PC5), J2.5
CREF_1: C1.1, IC1.22 (PC0)
CREF_2: C2.1, IC2.22 (PC0)
CREF_3: C4.1, IC3.22 (PC0)
GND: C1.2, C2.2, C4.2, C5.2, C6.2, C7.2, C8.2, C9.2, C10.2, C11.2, C12.2, C13.2, C14.2, C15.1, C16.1, C17.1, C18.1, C19.1, C20.1, C21.1, C22.1, C23.1, C24.1, C25.1, C26.1, C27.1, C28.1, C29.1, C30.2, D2.1 (K), D3.3 (VSS), IC1.2 (GND_1), IC1.8 (GND_2), IC1.25 (EP), IC2.2 (GND_1), IC2.8 (GND_2), IC2.25 (EP), IC3.2 (GND_1), IC3.8 (GND_2), IC3.25 (EP), IC4.3 (GND), J1.1, J2.1, J2.2, J2.3, J2.11, J2.12, J3.P6 (VSS), J5.1, J5.11, J6.2, J6.4, J6.5, J7.1, R6.2, R9.2, R12.2, S2.1, S2.2, S3.1, S3.2, U1.J1-2 (GND), U1.J1-9 (GND), U1.J2-2 (GND), U1.J2-7 (GND), U1.J2-9 (GND), U2.2 (GND), U2.17 (GND), U3.1 (GND)
I35: J5.6, U2.11 (I35)
IO32: J5.5, U2.10 (IO32)
IO33: J5.4, U2.9 (IO33)
LED_DATA: D3.4 (DIN), U2.8 (IO25)
unnamed: C6.1, IC1.7 (PTOUT), R4.2, R5.2, TP2.1
unnamed: C9.1, IC2.7 (PTOUT), R7.2, R8.2, TP6.1
unnamed: C12.1, IC3.7 (PTOUT), R10.2, R11.2, TP10.1
unnamed: D2.2 (A), R1.2
unnamed: IC1.5 (PT1), R4.1, TP1.1
unnamed: IC1.6 (PT0REF), R5.1
unnamed: IC1.19 (PCAUX), R6.1, TP3.1
unnamed: IC2.5 (PT1), R7.1, TP5.1
unnamed: IC2.6 (PT0REF), R8.1
unnamed: IC2.19 (PCAUX), R9.1, TP7.1
unnamed: IC3.5 (PT1), R10.1, TP9.1
unnamed: IC3.6 (PT0REF), R11.1
unnamed: IC3.19 (PCAUX), R12.1, TP11.1
PCAP1_EN: IC1.13 (IIC_EN), U1.J2-3 (IIC_EN), U2.3 (IO13/HSPI_MOSI)
PCAP1_INT: IC1.11 (PG5), U1.J2-5 (PG5), U2.6 (IO27)
PCAP2_EN: IC2.13 (IIC_EN), U2.5 (IO14/HSPI_CLK)
PCAP2_INT: IC2.11 (PG5), U2.7 (IO26)
PCAP3_EN: IC3.13 (IIC_EN), U2.18 (IO15/HSPI_CS0)
PCAP3_INT: IC3.11 (PG5), U2.20 (IO04)
PR1-SENSE: J2.20, R2.2, U2.13 (I39/SENSOR_VN)
PR2-SENSE: J2.10, R3.2, U2.14 (I36/SENSOR_VP)
SCL: IC1.16 (SCK_SCL), IC2.16 (SCK_SCL), IC3.16 (SCK_SCL), J5.12, U1.J2-6 (SCL), U2.29 (IO22/SCL)
SDA: IC1.15 (MOSI_SDA), IC2.15 (MOSI_SDA), IC3.15 (MOSI_SDA), J5.10, U1.J2-4 (SDA), U2.26 (IO21/SDA)
SD_CS: J3.P2 (CD/DAT3), U2.23 (IO05/VSPI_CS0)
SD_MISO: J3.P7 (DAT0), J5.8, U2.25 (IO19/VSPI_MISO)
SD_MOSI: J3.P3 (CMD), J5.7, U2.30 (IO23/VSPI_MOSI)
SD_SCLK: J3.P5 (CLK), J5.9, U2.24 (IO18/VSPI_CLK)
V_TEMP: IC4.2 (VOUT), U2.12 (I34)
Vcharge: J6.6, J7.2

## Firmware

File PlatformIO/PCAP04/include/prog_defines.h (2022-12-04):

#ifndef prog_defines_h
#define prog_defines_h

//Definitions for PCAP pins and addresses
#define pcap1_i2c 13        //I2C enable pin for 1st PCAP
#define pcap2_i2c 14        //I2C enable pin for 2nd PCAP
#define pcap3_i2c 15        //I2C enable pin for 3rd PCAP

#define pcap1_int 27        //DataIsReady from 1st PC
#define pcap2_int 26        //DataIsReady from 2nd PCAP
#define pcap3_int 04        //DataIsReady from 3rd PCAP

#define defaultAddress 0x28  //Default I2C address of PCAP04
#define pcap1_addr 0x29     //I2C address for 1st PCAP
#define pcap2_addr 0x2a     //I2C address for 2nd PCAP
#define pcap3_addr 0x2b     //I2C address for 3rd PCAP

//Definitions for indicator Leds and other interfaces
#define powerLed 27
#define ledR 26
#define ledG 26
#define ledB 26
#define ws2812Led 25
#define tempSensor 34
#define Vpos_C32 35 //commercial absolute pressure sensor
#define Vneg_C32 32 //commerical absolute pressure sensor

#define C32_sensitivity 23  //in mV/bar

//Definitions for SD-Card
#define SD_CS 5


#endif

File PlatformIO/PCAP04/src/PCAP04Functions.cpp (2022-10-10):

#include "PCAP04Functions.h"
#include <Arduino.h>

#include "prog_globals.h"
#include "prog_defines.h"

pcap_results_t* pcap_results;
pcap_status_t* pcap_status;

void pcap1_cdc_complete_callback(){
  pcap1.cdc_complete_flag = true;
  digitalWrite(ledG,HIGH);
}

void pcap2_cdc_complete_callback(){
  pcap2.cdc_complete_flag = true;
  digitalWrite(ledG,HIGH);
}

void pcap3_cdc_complete_callback(){
  pcap3.cdc_complete_flag = true;
  digitalWrite(ledG,HIGH);
}

void pcap04_configure_registers(PCAP04IIC &pcap, pcap_config_t * pcap_config, unsigned char i2cAddress){

  //Serial.println("current config");
  //pcap.print_config();

  *pcap_config = pcap.get_config();
  //Reg0 settings
  pcap_config->I2C_A = i2cAddress;          //Set I2C address to 43
  pcap_config->OLF_CTUNE = 0x01;            //Set low frequency clock
  pcap_config->OLF_FTUNE = 0x07;            //Finetune low frequency clock
  //Reg1 settings
  //Reg2 settings
  pcap_config->RDCHG_INT_SEL1 = 0x00;       //Discharge resistors PC4-PC5
  pcap_config->RDCHG_INT_SEL0 = 0x00;       //Discharge resistors PC0-3 plus PC6
  pcap_config->RDCHG_INT_EN = 0x01;         //Enable internal discharge resistors
  //Reg3 settings
  pcap_config->RCHG_SEL = 0x00;             //Charging resistors to limit charging
  //Reg4 settings
  pcap_config->C_REF_INT = 0x01;            //Use the internal reference
  pcap_config->C_COMP_EXT = 0x01;           //External cap compensation (DISABLE FOR NON FLOATING CAPS)
  pcap_config->C_COMP_INT = 0b1;            //Internal cap compensation
  pcap_config->C_DIFFERENTIAL = 0x00;       //No differential caps
  pcap_config->C_FLOATING = 0x01;           //Floating caps
  //Reg5 settings
  pcap_config->CY_HFCLK_SEL = 0x00;         //Low frequency clock (50 kHz)
  //Reg6 settings
  pcap_config->C_PORT_EN = 0x3F;
  //Reg7:8 settings
  pcap_config->C_AVRG = 0x0d;               //Samples to take average from
  //Reg11:9
  pcap_config->CONV_TIME = 0x2710;          //Conversion time (10000)
  //Reg12 settings
  pcap_config->DISCHARGE_TIME = 0x10;       //Discharge time (x*50 kHz)
  //Reg13 settings
  pcap_config->C_STARTONPIN = 0x02;         //Pin that triggers a CDC measurement (only if trig enabled)
  pcap_config->C_TRIG_SEL = 0x02;           //Timer triggered reading
  //Reg14 settings
  pcap_config->PRECHARGE_TIME = 0x10;       //Precharge time (x*50 kHz)
  //Reg15 settings
  pcap_config->C_FAKE = 0x04;               //Number of "fake" or "warm-up" measurements before "real"
  //Reg16 Settings
  pcap_config->FULLCHARGE_TIME =  0x10;     //Time to charge without I_lim
  //Reg17 settings
  pcap_config->C_REF_SEL = 0;  //Reference capacitances (0 = min, 1 = 1pF ... 31 = 31 pF)
  //Reg18 settings
  pcap_config->C_G_EN = 0b010110;           //Guard enabled for ports
  //Reg19 settings
  pcap_config->C_G_OP_VU = 0;               //Gain for the guard (0 = 1.00, 3 = 1.03)
  //Reg20 settings
  pcap_config->C_G_OP_TR = 7;               //Guard OP current trim
  //Reg21 settings
  pcap_config->R_TRIG_PREDIV = 0x0a;
  //Reg22 settings
  pcap_config->R_TRIG_SEL = 0x05;           //Trigger for RDC. 5 = asynchronous at end of CDC
  pcap_config->R_AVRG = 0x00;               //Sample size for mean value
  //Reg23 settings
  pcap_config->R_PORT_EN = 0b00;            //Activate R_PORTS, bit0 = PT0REF, bit1 = PT1
  pcap_config->R_PORT_EN_IMES = 0b1;        //Activate internal aluminium temp sensor
  pcap_config->R_PORT_EN_IREF = 0b1;        //Activate internal reference resistor
  pcap_config->R_FAKE = 0x00;               //Number of "fake" or "warm-up" measurements before "real"
  //Reg24, 25, 26 settings (Mandatory bits)
  //Reg27-29 settings
  //Reg30 settings
  pcap_config->PG5_INTN_EN = true;          //Route INTN signal to PG5
  //Reg35 settings
  pcap_config->CDC_GAIN_CORR = 0x40;        //Firmware defined gain correlation factor
  //Reg29 settings

  //Reg42 settings
  pcap_config->EN_ASYNC_READ = 0;           //Enable Synchronised read (Update results based on pin interrupt)


  pcap.update_config(pcap_config);

  //Serial.println("updated config");
  //pcap.print_config();

}

void initialisePCAP(PCAP04IIC * pcap, pcap_config_t * configuration,int pcap_i2c, unsigned char pcap_addr){
  int pcap_addr_conf = 0x00;
  pcap->update_address(defaultAddress);
  //Enable I2C on the selected device
  digitalWrite(pcap_i2c, HIGH);


  while (pcap->test_connection() == false){  //Test if connection can be made with the default address
    Serial.println("Default address failed, trying with already correct address");
    pcap->update_address(pcap_addr);             
    if (pcap->test_connection() == true){    //Test if the connection can be made with the already changed address
      pcap->send_command(POR_RESET);         //Do a power on reset to reset the address
      pcap->update_address(defaultAddress);
      break;
    }
    pcap->update_address(defaultAddress);

    Serial.println("Connection to PCAP04 failed!! Retrying in 3 second");
    digitalWrite(ledR,HIGH);
    delay(3000);
  }

  //Connection has been made begin initialisation sequence
  Serial.println("\n Initialising PCAP04");
  digitalWrite(ledR,LOW);
  digitalWrite(ledB,HIGH);

  pcap->init_nvram();
  pcap04_configure_registers(*pcap, configuration,pcap_addr_conf);
  pcap->initializeIIC();

  // //Change the I2C address from default to the correct address of the PCAP
  // pcap_addr_conf = pcap_addr & 0b011;       //Apply the new address in the configuration
  // Serial.println("Changing address to " + (String)pcap_addr);
  // pcap04_configure_registers(*pcap, configuration,pcap_addr_conf);
  // pcap->send_command(CDC_START);
  // pcap->update_address(pcap_addr);

  // //Test the connection again, see if the address change was successfull
  // while (pcap->test_connection() == false){
  //   Serial.println("Address change of PCAP04 failed!! Retrying to connect in 3 second");
  //   digitalWrite(ledR,HIGH);
  //   delay(3000);
  // }
  digitalWrite(pcap_i2c, LOW);
}

void updateResults(PCAP04IIC * pcap, int pcapIndex, int pcap_i2c){
  digitalWrite(pcap_i2c, HIGH);
  digitalWrite(ledG, LOW);
  digitalWrite(ledR, HIGH);
  pcap_status = pcap->get_status(false);
  pcap->cdc_complete_flag = false;
  pcap_results = pcap->get_results();

  // Serial.print("PCAP "+ (String)pcapIndex + ": ");
  // Serial.println(pcap_results->C1_over_CREF);

  current_micros = millis();
  if (pcap_status->COMB_ERR){
    Serial.println("OUTPUT ERROR IN PCAP04-" + String(pcapIndex+1));
    return;
  }
  resultArray[pcapIndex][0][0] = (pcap_results->C0_over_CREF * multiplicationFactors[pcapIndex] - zeroingFactors[pcapIndex][0]);
  resultArray[pcapIndex][1][0] = (pcap_results->C1_over_CREF * multiplicationFactors[pcapIndex] - zeroingFactors[pcapIndex][1]);
  resultArray[pcapIndex][2][0] = (pcap_results->C2_over_CREF * multiplicationFactors[pcapIndex] - zeroingFactors[pcapIndex][2]);
  resultArray[pcapIndex][3][0] = (pcap_results->C3_over_CREF * multiplicationFactors[pcapIndex] - zeroingFactors[pcapIndex][3]);
  resultArray[pcapIndex][4][0] = (pcap_results->C4_over_CREF * multiplicationFactors[pcapIndex] - zeroingFactors[pcapIndex][4]);
  resultArray[pcapIndex][5][0] = (pcap_results->C5_over_CREF * multiplicationFactors[pcapIndex] - zeroingFactors[pcapIndex][5]);
  // resultArray[pcapIndex][0][0] = &pcap_results->C0_over_CREF;
  // resultArray[pcapIndex][0][0] = &pcap_results->C0_over_CREF;
  // resultArray[pcapIndex][1][0] = &pcap_results->C1_over_CREF;
  // resultArray[pcapIndex][2][0] = &pcap_results->C2_over_CREF;
  // resultArray[pcapIndex][3][0] = &pcap_results->C3_over_CREF;
  // resultArray[pcapIndex][4][0] = &pcap_results->C4_over_CREF;
  // resultArray[pcapIndex][5][0] = &pcap_results->C5_over_CREF;

  //resultIndexes[pcapIndex] = resultIndexes[pcapIndex] + 1;
  // if (resultIndexes[pcapIndex] > sizeof(resultArray[pcapIndex][0][resultIndexes[pcapIndex]])/sizeof(float) - 1)
  // {
  //   resultIndexes[pcapIndex] = 0;
  // }
  
  newResults = true;
  digitalWrite(ledR, LOW);
  digitalWrite(pcap_i2c, LOW);

}


void printResults(){
  if (pcap1_enable == true){
    Serial.print("1st PCAP:");
    for (int i = 0; i < 6; i++){
      Serial.print("\t");Serial.print(resultArray[0][i][0],9);
    }
    Serial.println("");
  }
  if (pcap2_enable == true){
    Serial.print("2nd PCAP:");
    for (int i = 0; i < 6; i++){
      Serial.print("\t");Serial.print(resultArray[1][i][0],9);
    }
    Serial.println("");
  }
  if (pcap3_enable == true){
    Serial.print("3rd PCAP:");
    for (int i = 0; i < 6; i++){
      Serial.print("\t");Serial.print(resultArray[2][i][0],9);
    }
    Serial.println("");
  }
  Serial.println("");
}

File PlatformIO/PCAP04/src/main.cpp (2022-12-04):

#include <Arduino.h>
#include "pcap04IIC.h"
#include <Adafruit_NeoPixel.h>
#ifdef __AVR__
#include <avr/power.h> // Required for 16 MHz Adafruit Trinket
#endif

#include "prog_types.h"
#include "prog_globals.h"
#include "prog_defines.h"

#include "SDFunctions.h"
#include "webserverFunctions.h"
#include "PCAP04Functions.h"

//------------Parameters------------//

//Default wifi connection settings
String ssid = "GenericWifi-SSID";
String password = "GenericWifi-PWD";
String hostname = "espui";

//SD and configuration settings
bool SD_attached = false;
const char* generalConfig = "/generalConfiguration.txt";
const char* config1 = "/configPCAP1.txt";
const char* config2 = "/configPCAP2.txt";
const char* config3 = "/configPCAP3.txt";

//Enable PCAP devices
bool pcap1_enable = true;
bool pcap2_enable = true;
bool pcap3_enable = true;

//------------Variables------------//

//Configuration structures for each PCAP
pcap_config_t Config_PCAP_1;
pcap_config_t Config_PCAP_2;
pcap_config_t Config_PCAP_3;

//Initialisation of each PCAP chip
PCAP04IIC pcap1(pcap04_version_t::PCAP04_V1,pcap_measurement_modes_t::STANDARD,defaultAddress,Config_PCAP_1);
PCAP04IIC pcap2(pcap04_version_t::PCAP04_V1,pcap_measurement_modes_t::STANDARD,defaultAddress,Config_PCAP_2);
PCAP04IIC pcap3(pcap04_version_t::PCAP04_V1,pcap_measurement_modes_t::STANDARD,defaultAddress,Config_PCAP_3);

//Variables to print the time on SD and keep a correct timeout for the webserver
unsigned long current_micros = 0;
unsigned long previous_micros = 0;
unsigned long current_epoch = 0;
unsigned long incremented_millis = 0;

//Factors to zero out results and account for inaccuracies of reference capacitances
bool updatedFactors = false;
float zeroingFactors[3][6] = { 0 };
float multiplicationFactors[3] = {1,1,1};

//Arrays for the results
int resultIndexes[3] = {0,0,0};
float resultArray[3][6][9] = { 0 };
bool newResults = false;
bool initialisation = true;

float currentTemperature = 0;
float currentPressure = 0;
Adafruit_NeoPixel indicatorLed(1,ws2812Led, NEO_GRB + NEO_KHZ800);

float readTemperature(){
  //MCP9701 temperature sensor
  //Conversion from voltage to temperature: Vout = Tc * Ta + V0c
  //Tc = Temperature coefficient, Ta = ambient temperature, V0c = sensor output at 0 celcius
  //so: Ta = (Vout-V0c)/Tc

  //remap ADC to a voltage output in mV 
  //Taking into account that the ADC works best in the range of 0.1 to 3.2V (https://randomnerdtutorials.com/esp32-adc-analog-read-arduino-ide/)
  float sensorInput = map(analogRead(tempSensor),0,4095,100,3200); 
  float ambientTemperature = (sensorInput-400)/19.5;

  currentTemperature = ambientTemperature;
  return ambientTemperature;
}

float readPressureCommercial(){
  //Read the absolute pressure from a commercial C32 pressure sensor as a reference pressure sensor
  //The sensor is configured as a Wheatstone bridge, so two inputs will be read

  float C32_pos = map(analogRead(Vpos_C32),0,4095,100,3200);  //Converted from analogRead to mV
  float C32_neg = map(analogRead(Vneg_C32),0,4095,100,3200);  //Converted from analogRead to mV

  float V_pressure = C32_pos-C32_neg;
  V_pressure = V_pressure * 3.3 / 5;  //Convert from 5V to 3.3V operating
  
  currentPressure = V_pressure / C32_sensitivity;
  return currentPressure;
}

void updateWS2812(int brightness, int R, int G, int B){
  indicatorLed.setBrightness(brightness);
  indicatorLed.setPixelColor(0,indicatorLed.Color(R,G,B));
  indicatorLed.show();
}

void setup() {
  //Startup esp32 and begin serial connection
  Serial.begin(115200);
  Serial.println("ESP32 has started, initialising connection...");

  //Setup pins for indicator lights and update pins
  pinMode(ws2812Led, OUTPUT);
  pinMode(pcap1_int, INPUT);
  pinMode(pcap2_int, INPUT);
  pinMode(pcap3_int, INPUT);
  pinMode(tempSensor, INPUT);
  pinMode(Vpos_C32, INPUT);
  pinMode(Vneg_C32, INPUT);

  indicatorLed.begin();
  updateWS2812(50,0,255,0);

  //Make sure all PCAP chips are disabled
  pinMode(pcap1_i2c, OUTPUT);
  pinMode(pcap2_i2c, OUTPUT);
  pinMode(pcap3_i2c, OUTPUT);

  digitalWrite(pcap1_i2c, LOW);
  digitalWrite(pcap2_i2c, LOW);
  digitalWrite(pcap3_i2c, LOW);


  //Initialise the SD-card
  delay(100);
  SD_Initialise();

  setupConnection(ssid, password, hostname);
  setupWebserver();
  time_t timeSinceEpoch = 1666051200;
  struct timeval now = { .tv_sec = timeSinceEpoch};
  settimeofday(&now, NULL);

  //Setup the webserver and show that the device is initialising
  ESPUI.updateLabel(webserverIDs.STATUS,"Initializing");
  ESPUI.begin("ESPUI Control");

  updateWS2812(100,255,255,0);
  //Initialise the PCAP chips (only the ones that are enabled)
  if (pcap1_enable == true){
    Serial.println("Initializing 1st PCAP");
    initialisePCAP(&pcap1, &Config_PCAP_1, pcap1_i2c, pcap1_addr);
    attachInterrupt(digitalPinToInterrupt(pcap1_int),pcap1_cdc_complete_callback,FALLING);
    Serial.println("1st PCAP04 has been connected and is initialised");
    ESPUI.updateLabel(webserverIDs.STATUS,"1st PCAP04 has been initialised");
    delay(300);
  }
  updateWS2812(100,255,255,85);

  digitalWrite(pcap1_i2c, LOW);
  digitalWrite(pcap2_i2c, LOW);
  digitalWrite(pcap3_i2c, LOW);
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

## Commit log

2022-07-07 Changed initialisation led color to blue
2022-07-07 Added pinout image of ESP32
2022-08-02 Created Measurement PCB
    [PCAP04-IC.kicad_sch, PCAP04_Interface.kicad_pcb, PCAP04_Interface.kicad_sch]
2022-08-02 Edited PCB so battery is on the back
    [PCAP04_Interface.kicad_pcb]
2022-08-02 Added logos and text on PCB
    [PCAP04_Interface.kicad_pcb]
2022-08-02 Added breakout for C1.5 and C2.5, updated readme
    [PCAP04_Interface.kicad_sch]
2022-08-02 Added breakout for C1.5 and C2.5
    [PCAP04_Interface.kicad_pcb]
2022-08-03 Created simple webserver, updated PCB
2022-08-04 Created PlatformIO-based project
    [PCAP04_Interface-B_Cu.gbr, PCAP04_Interface-B_Mask.gbr, PCAP04_Interface-B_Paste.gbr, PCAP04_Interface-B_Silkscreen.gbr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]
2022-08-05 Upgraded webserver functionalities
    [PCAP04_Interface.kicad_pcb, PCAP04_Interface.kicad_sch]
2022-08-16 Poging tot config
    [PCAP04_Interface.kicad_pcb, PCAP04_Interface.kicad_sch]
2022-09-05 Changed battery circuitry
    [Farnell_Order_List.xlsx, PCAP04_Interface-B_Cu.gbr, PCAP04_Interface-B_Mask.gbr, PCAP04_Interface-B_Paste.gbr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]
2022-09-05 Changed Boost circuit
    [Farnell_Order_List.xlsx, PCAP04_Interface-B_Cu.gbr, PCAP04_Interface-B_Mask.gbr, PCAP04_Interface-B_Paste.gbr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]
2022-09-05 Updated PCB images for readme
2022-09-05 Updated readme to the current state
2022-09-05 The readme is updated to the current state
2022-09-05 Edited order list for components
    [Farnell_Order_List.xlsx]
2022-09-06 Started on framework for multiple PCAP04 devices
2022-09-07 Webserver config allows for multiple PCAP devices
2022-09-15 Updated PCB slightly
    [PCAP04_Interface.kicad_sch]
2022-09-16 Updated calibration features
2022-09-20 Improved extra configuration features
    [Calibration.xlsx]
2022-09-21 Added temperature readout
    [Calibration.xlsx]
2022-09-23 Added WS2812 functionality as indicator led
2022-12-04 Added readout of commercial pressuresensor
